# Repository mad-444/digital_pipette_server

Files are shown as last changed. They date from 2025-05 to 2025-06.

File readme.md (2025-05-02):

# Digital Pipette Server

This repo contains code to run the [science-jubilee](https://science-jubilee.readthedocs.io/en/latest/index.html)  implementation of the [Digital Pipette](https://doi.org/10.1039/D3DD00115F) tool. `digital_pipette.py` contains methods to manage state and perform actions with individual syringe tools. `serve_pipette.py` exposes this funcitonality for multiple syringes as an HTTP api. This service is intended to interface with the [science-jubilee HTTPSyringe tool](https://github.com/machineagency/science-jubilee/blob/main/src/science_jubilee/tools/HTTPSyringe.py). See the [documentation] for this tool for more information on required hardware and instructions to configure the tool with a Jubilee. Brief instructions for configuring and running the service are included here. 

## Implementation notes

The digital syringe tool uses a servo linear actuator to move the plunger of a syringe to perform liquid handling tasks. Code in this repo is responsible for managing the positioning of the actuator/plunger system to deliver desired volumes of liquids. The [companion tool definition over at science-jubilee](https://github.com/machineagency/science-jubilee/blob/main/src/science_jubilee/tools/HTTPSyringe.py) is reponsible for positioning the syringe tool in the correct location on the deck to perform the desired liquid handling task. 

Servo motors use a closed loop feedback system to control positioning. Position is controlled by sending timed voltage pulses. The length of the 'high' pulse tells the servo where to move. Generally a 1000us pulse is fully closed, 2000us is fully open, and intermediate values set position between these limits. This implementation uses the [pigpio library](https://abyz.me.uk/rpi/pigpio/index.html) to handle the servo control. The DigitalPipette object translates requests to dispense or aspirate a particular volume into a servo pulsewidth by 1) converting the volume into a pulswidth change using a conversion factor defined in a config.json file, 2) Adding/subtracting the pulswidth change to the current servo pulsewidth value (ie, current servo/syringe position), and 3) Updating the servo pulsewidth signal so the motor moves to then new position. Speed control of the movement is accomplished by moving the servo through a series of small timed intermediate movements.

## Setup
 
### Requirements

You will need:
- A raspberry pi (assuming a model 4B here, anything should work in theory) running raspberry pi OS and set up with a known static ip address. 
- A digital_syringe tool, built and wired according to the [science-jubilee documentation](https://science-jubilee.readthedocs.io/en/latest/building/http_syringe.html#). 

### Installation
1. Set up and activate a new [python venv](https://docs.python.org/3/library/venv.html) for this project.
2. Install pigpio following [their instructions](https://abyz.me.uk/rpi/pigpio/download.html). Install this in a separate directory from the `digital_pipette_server` repo. 
3. Clone this repository
4. Install the `digital_pipette_server` dependencies in `requirements.txt` by running `pip install -r requirements.txt` from the root of the digital_pipette_server repo.

### Configuration
For now, you will set some initial configuration constants to get the tool to a usable state. These constants are not correct and you need to be careful to not overextend the servo motor to avoid damaging the motor or your syringe. Setting them up first allows you to move the syringe and determine correct values. 

1. You will need to set up a config.json file for each syringe tool you have. The `example_config.json` file is a template.  You will need to set:
- us_per_uL: conversion factor, the change in pulsewidth (in microseconds) to dispense 1 microliter. Obtain this with a gravimetric calibration or linear interpolation from full and empty positions (see below). For now, set this to `0.1`
- gpio_pin: The pi GPIO pin that the signal wire of the servo is plugged into. 
- name: name of the syringe tool, used to id the syringe in API requests.
- full_position: The pulsewidth of the servo when the syringe is full. Obtain through trial and error. Set to `1000` for now. 
- empty_position: The pulsewidth of the servo when the syringe is empty. Obtain through trial and error. Set to `2000` for now. Once you calibrate the tool,  set this constant so the syringe plunger bottoms out on the bottom of the barrel, but isn't squished too much.
- capacity: total capacity of the syringe between empty_position and full_position in microliters
- time_step_size: Resolution of movement steps for speed controlled movements. Suggested default of 0.1
- min_pw_step: Minimum pulsewidth step to make when performing speed controlled move. Suggested minimum of 3, too small and the servo will stall

2. Edit the `serve_piptte.py` file to instantiate a DigitalPipette instance for your new pipette and add it to the `pipettes` dictionary. You will need to do this for each pipette tool you are defining.
   
```
example_pipette = digital_pipette.DigitalPipette.from_config('~/digital_pipette_server/example_config.json')
logger.info('Instantiated pipette_10cc_1')

pipettes = {'example_pipette':example_pipette, ... }
```

### Starting the service
1. Start the [pigpio dameon](https://abyz.me.uk/rpi/pigpio/pigpiod.html) which allows this service to set pulsewidths: ` 
```
sudo pigpiod
```

2. Start the flask app to serve the endpoint:
```
flask --app serve_pipette run
```

Note: if flask command does not let curl commands received, try running the app through python by:
```
python serve_pipette.py
```
### Setting the pi up for headless use

It is ideal to set up pgpiod and the flask app as system services so they start on startup. Registering them as system services will enable this.

1. Enable pigpiod as a system service:
```
sudo systemctl enable pigpiod
```

2. Create a new service file for the flask app at `/etc/systemd/system/'. Name it `pipette-service.service`

3. Enter the following into this file. Note the filepaths to edit
```

[Unit]
Description=pipette server
After=network-online.target
Wants=network-online.target

[Service]
WorkingDirectory=$<absolute path to this repo>/digital_pipette_server
ExecStart=$<absolute path to your venv for this project>/servo/bin/python serve_pipette.py
Restart=always

[Install]
WantedBy=basic.target

```

4. Enable the service with `sudo systemctl enable pipette-service`

Reboot. The app should now come online automatically at boot. 

---
This completes the software installation of the digital_pipette server. If you are installing this tool on a science-jubilee, return to the science-jubilee HTTPsyringe tool documentation to complete setup. 
---
Standalone usage without science-jubilee:

### Loading a syringe
After you start the service, you will need to "load" your syringes before they can be used. This is needed to tell the DigitalPipette python object where it's plunger/actuator system is. It is set up this way instead of doing a homing procedure so that you can load a syringe manually before installing it into the syringe tool. You load a syringe in software by calling the `/load_syringe` route with the current volume and pulsewidth of the syringe. Send a POST request to `/load_syringe` with the json payload {"name":$<syringe_name>, "volume":$<current syringe volume>, "pulsewidth":$<current syringe pulsewidth>"}. Anywhere there is a $<notes>, replace it (including $<>) with your values. The POST request is made through curl. The example command for loading syringe looks like this:

```
curl -d '{"name":$<syringe_name>, "volume":$<current syringe volume>, "pulsewidth":$<current syringe pulsewidth>"}' -X POST http://RaspberryUserName@192.168.0.0:5000/load_syringe -H "Content-Type: application/json"
```

How do you know the current pulsewidth? You probably need to set it first. Do that with the `/set_pulsewidth` route. POST a request here with json payload {"name":$<syringe_name>, "pulsewidth":$<desired pulswidth>", "speed":$<speed to move in uL/s>}.

[!WARNING]
If you don't set the pulsewidth to the correct current pulsewidth when calling the `/load_syringe` route, your first dispense volume will be inaccurate as the movement is calculated off of the current position. Weird things (ex aspirating when you mean to dispense) can also occur when pulsewidth is set incorrectly due to the intermediate movements set by the speed control. 

### Using the syringe
Once the syringe is loaded, it can be used to aspirate and dispense liquids. Aspirate (suck up liquid) with the `/aspirate` endpoint and dispense (push out liquid) with the `/dispense` endpoint. For both, POST a json payload containing {"name":$<syringe name>, "volume":$<volume in uL to aspirate/dispense>, "speed":$<speed to move in uL/S>}. All positioning of the syringe is handled separately, for example by using the science-jubilee HTTPsyringe tool versions of the aspirate and dispense methods.

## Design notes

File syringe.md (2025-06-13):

Materials

-   Raspberry pi 4 8GB
    
-   6V DC power supply
    
-   Panel mount barrel jack receptacle
    
-   Power distribution block
    
-   Linear servo actuator, Actuonix L16-100-63-6-R
    
-   M12 4-pin connector
    
-   M12 4-pin panel mount socket
    
-   M3 brass heat set inserts
    
-   22g Hookup wire
    
-   1/8” expandable wiring sleeve
    
-   Misc. M3 and M4 hardware
    
-   Jubilee tool vitamins (wedge plate and tool balls)

### Software

Directions for initiating the flask server on the Pi and configuring it for headless use for syringe control can be found [here](https://github.com/pozzo-research-group/digital_pipette_server/blob/main/readme.md)

Other Jubilee documentation can be found [here](https://science-jubilee.readthedocs.io/en/latest/index.html)

Additional documentation for the software can be found on the [github](https://github.com/machineagency/science-jubilee)

General recommendations

-   Ensure a static IP for the raspberry pi has been set

#### Required Imports

```python

from science_jubilee.Machine import Machine

from science_jubilee.tools import HTTPSyringe

from science_jubilee.decks import Deck # necessary for using labware

```

#### Prompts

```python

m = Machine(address = 'xxx.xxx.x.xx') # ip address of jubilee

m.load_tool(syringe_name)

deck = m.load_deck("deck_name")

syringe_name = HTTPSyringe.HTTPSyringe.from_config(2, '/home/clgould99/science-jubilee/src/science_jubilee/tools/configs/20_cc_glass1.json')

# file path to config file of the syringe

syringe_name.load_syringe(400, 1500) # set syringe location somewhere in the middle to start

# slowly jog the pulsewidth up and down to find your syringe's empty and full positions.

syinge_name.set_pulsewidth(1500, s = 200)

syringe_name.aspirate(volume, jubile_labware_location_to_aspriate_from) # aspirate command

```

Adjustments to duet configuration files

-   Tool post location
    
-   Set offsets so that there is no interference between syringe and other components

### Syringe Construction

1.  Heat set 7 M3 brass heat inserts. The preferred method for this was to pick up the heat insert using a soldering iron and then apply gentle downward pressure until the inserts were in the correct position The locations are shown below in red. Next, screw in 3 tool balls (shown below in blue).


2.  Screw the tool holder plate into the syringe holder


3.  Use 3 more heat inserts to secure the tool holder locking mechanism (wedge plate).


4.  Place 4 rubber O-rings on the wings.


5.  Install 2 m3 brass heat inserts on the tool holder bracket


7.  Screw in the syringe plunger holder and secure using hex nut

    
10.  Install the actuator


8.  Slot the syringe into place and secure using 2 m4 screws


### Control Box Construction

1.  Solder 22 gauge wire of a length approximately 7” to M12 4 Pin Male


2.  Place threaded barrel jack power adapter through hole in control box pictured below
    
3.  Connect the 22 gauge wire in step 2 to ports A1 and B1 by unscrewing and rescrewing corresponding screws


4.  Repeat steps 1-3 for each additional syringe/pipette unit
    
5.  Screw power distribution block into standoffs housing using M.2 6mm screws

6.  Connect power distribution block to Threaded Barrel Jack power adapter


7.  Connect male M12 4 Pin to female m12 4 pin and attach to linear actuator (note that that the pins that the 22 gauge wires are connected to on the male need to match the pins that coming of out of the female connector)


8.  Connect power, ground, and input to raspberry pi. Any signal GPIO pin can be used as long it is correctly indicated on the configuration file. Refer to Raspberry Pi documentation for pinout.


9.  Install in control box as shown below after testing (May need to remove heatsink from Pi)


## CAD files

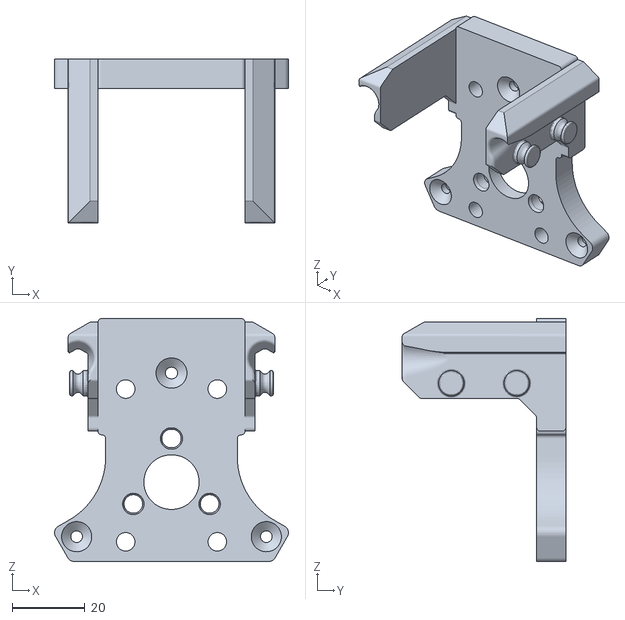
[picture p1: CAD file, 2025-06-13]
tool_holder.stl
64.3 x 45.0 x 66.8

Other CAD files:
syringe_holder.f3z

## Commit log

2024-07-11 initial prototype completion
2024-07-18 modify api to support multiple syringe tools
2024-08-15 config updates for current config
2024-08-15 add logging and voltage/speed control to digital syringe tool
2024-08-20 remove adafruit potentiometer control from serve pipette.py
2024-08-26 debug syringe server
2025-01-14 set up for new syringe
2025-01-16 init setup new glass syringes
